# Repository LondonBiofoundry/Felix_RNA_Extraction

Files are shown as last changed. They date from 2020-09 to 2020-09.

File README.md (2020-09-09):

# Felix_RNA_Extraction
Extraction script for running RNA extraction using multiple manufacturer kits

# Hardware requirements
- CyBio FeliX Liquid Handler (Analytik Jena OL5015-24-100)
- 1x CyBio Head R96/1000 μl (Analytik Jena*)
- 2x 96-channel magazine (Analytik Jena OL3396-352-25*)
- 2x 97 mm Support (Analytik Jena OL3317-11-105*)
- 1x CyBio FeliX Gripper (Analytik Jena*)
- 1x 37 mm Support (Analytik Jena OL3317-11-120*)
- 1x Magnum FLX Enhanced magnet adapter (Alpaqua*)
- 1x BioShake D30-T elm with deep well adapter (QInstruments 2016-0518; note: *not* included in Extraction Set)
- 1x Magic Tip Thing (one or two spares are probably desirable, 3D-printed STL file included in repository)
- Laptop with a minimum of two USB ports, running Windows (Windows 10 has been confirmed to work)

&ast; included in Analytik Jena Extraction Set OL5015-25-120

# Consumable requirements per kit
- 2x 1000 μl Tecan-style filter tips (Analytik Jena OL3811-25-939-F)
- 2x protective plate (Analytik Jena 31-01641)
- 7x 96-well 2 ml deep-well plates (e.g. ThermoFisher KingFisher Flex A43075)
- 1x 96-well elution plate (e.g. FrameStar 96 well skirted PCR plate 4titude 4ti-0960)
- 1x 96 reaction extraction kit (see below for supported kits)

# Software
- Analytik Jena Composer - with support for Bioshake D30-T elm and CyBio Head R96/1000 μl, confirmed with Windows 10
- Extraction script (v16.bms)

# Supported Extraction Kits
- innuPREP Virus DNA/RNA Kit - FX (Analytik Jena 845-FX-2096096, 845-KS-4800)
- Maxwell HT Viral TNA - Custom (Promega AX2340)

# Instructions
- the file `instructions.pdf` describes the procedure for preparing with the innuPREP Virus DNA/RNA kit or the Maxwell HT Viral TNA kit.

# 3D printing
- the Magic Tip Thing permits a more reliable transfer of tips from their packaging into the magazine
- printed using an FDM printer (Prusa MK3S) with 0.2 mm layer height, no supports
- print the files `Ejector.stl` and `Retainer.stl` which will slot into each other when in use

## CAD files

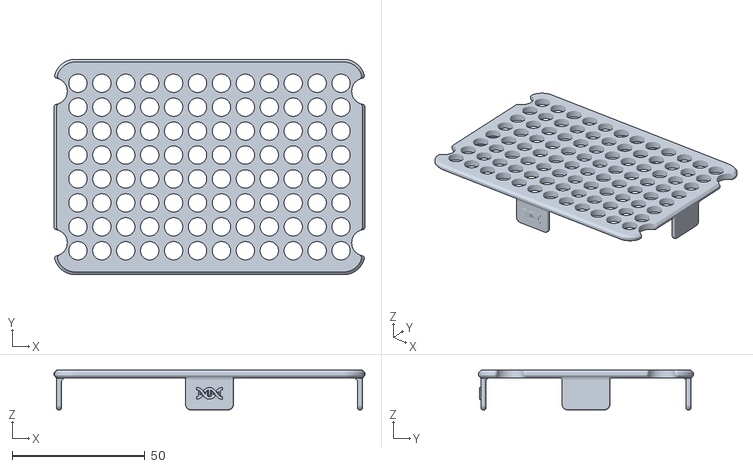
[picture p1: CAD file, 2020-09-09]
Ejector.stl
117.0 x 81.0 x 15.0

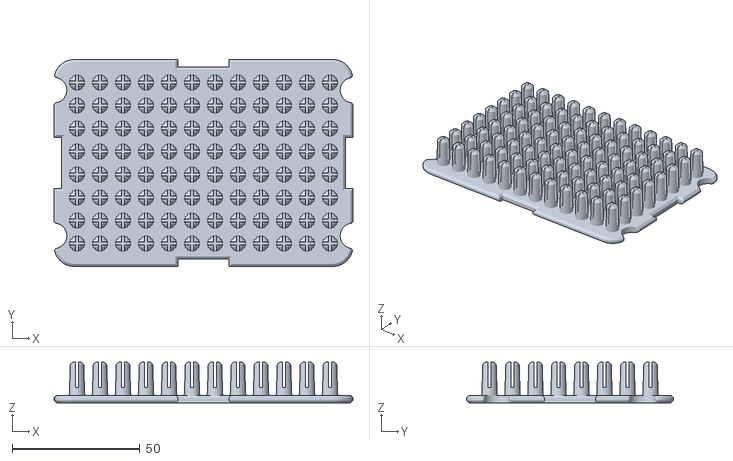
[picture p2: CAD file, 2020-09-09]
Retainer.stl
117.0 x 81.0 x 16.0

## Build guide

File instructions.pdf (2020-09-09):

Automated RNA extraction using a Felix liquid handling robot

Current version: | 16
Last updated: | April 24, 2020
Kits: | innuPREP Virus DNA/RNA Kit – FX (Analytik Jena)
| Maxwell HT Viral TNA (Promega)
The M⁴
team: | Marta Ciechonska, Michael Crone,
| Miles Priestman, Marko Storch
Contact for support: m.priestman13@imperial.ac.uk

## Contents

1 Preparing tips | 2
2 innuPREP Virus DNA/RNA Kit (Analytik Jena) | 3
3 Maxwell HT Viral TNA Kit (Promega) | 7
4 Running the protocol | 10
5 Troubleshooting | 11

1

Automated RNA extraction using a Felix liquid handling robot

## 1 Preparing tips

Prepare 2 × 1000 µl tip trays:

– Prepare the 97 mm metal support (OL3317-11-105) by placing the plastic tip protector into the base (this prevents cross-contamination). – Open the plastic tip box.
– Place the tip converter (OL3396-352-25) over the top of the tips.
– Invert the box onto a flat surface.
– Remove the white plastic insert from the tips.
– Slide the black magazine (OL3810-13-024) over the tips, with the metal rods pointing downwards.
– Invert the tips again, and remove the tip converter.
– Place the tips onto the 97 mm metal support.
– Place the supported tips into the Felix at positions 2 or 5 (centre of the lower deck).

Proceed to prepare input plates according to which kit you are using, there are minor dierences so please double-check you are following the correct section.

Automated RNA extraction using a Felix liquid handling robot

## 2 innuPREP Virus DNA/RNA Kit (Analytik Jena)

Manufacturer: AnalytikJena
Cat No: | 845-KS-4800

Please note that the protocols for a 400 µl sample volume and a 200 µl sample volume are dierent.

Note the dierent volume of Carrier Mix added to Lysis Solution V.

The 200 µl protocol also uses one less plate (Plate 3). For simplicity, the plate numbering system is preserved between all protocols to aid in placement on the Felix deck.

### 2.1 Kit preparation

Prepare the innuPREP Virus DNA/RNA Kit contents as necessary:

– Add 1.5 ml ddH2O to the vial of lyophilised proteinase K, mix thoroughly, store at −20 ◦C.
– Add 1.25 ml RNase-free water to the vial of lyophilised Carrier Mix, mix thoroughly, store at −20 ◦C; do not freeze/thaw more than 3 times.
– Add 72 ml absolute ethanol to Washing Solution B2, mix thoroughly. – Vigorously shake MAG suspension, or vortex for 30 s before use.

### 2.2 Plate preparation – 400 µl sample volume

Make sure that you are using 400 µl sample volume, otherwise, skip to Section 2.3: Plate preparation – 200 µl sample volume (pg. 4)

– Add 1.3 ml Carrier Mix to 52 ml Lysis Solution V, store at 4

◦C (maximum
7 days).

Prepare 96-well deep-well plates (provided in the kit):

Automated RNA extraction using a Felix liquid handling robot

Plate 1: Lysis/Sample

– 400 µl Lysis Solution/Carrier Mix – 400 µl liquid sample
– 50 µl proteinase K

Plate 2: Process

– 450 µl Binding Solution V – 50 µl MAG Suspension

Plate 3: Binding

– 450 µl Binding Solution V

Plate 4: Washing Solution A

– 1100 µl Washing Solution A

Plate 5: Washing Solution B2

– 1100 µl Washing Solution B2

Plate 6: Elution

– Leave empty

Plate 7: Water

– 600 µl RNase-free water

Prepare Plate 8: Final elution which can be an empty 96-well PCR plate (any 96-well labware should work, but please confirm before trying new plates).

### 2.3 Plate preparation – 200 µl sample volume

Make sure that you are using 200 µl sample volume, otherwise, skip to Section 2.2: Plate preparation – 400 µl sample volume (pg. 3)

– Add 1.75 ml Carrier Mix to 35 ml Lysis Solution V, store at 4

◦C (maximum 7 days).

Prepare 96-well deep-well plates (provided in the kit):

Automated RNA extraction using a Felix liquid handling robot

Plate 1: Lysis/Sample

– 200 µl Lysis Solution/Carrier Mix – 200 µl liquid sample
– 50 µl proteinase K

Plate 2: Process

– 450 µl Binding Solution V – 50 µl MAG Suspension

Plate 4*: Washing Solution A

(*Plate 3 is omitted)
– 1100 µl Washing Solution A

Plate 5: Washing Solution B2

– 1100 µl Washing Solution B2

Plate 6: Elution

– Leave empty

Plate 7: Water

– 600 µl RNase-free water

Prepare Plate 8: Final elution which can be an empty 96-well PCR plate (any 96-well labware should work, but please confirm before trying new plates).

### 2.4 Deck layout

Place plates onto the Felix according to the scheme below.

Automated RNA extraction using a Felix liquid handling robot

Bottom Deck

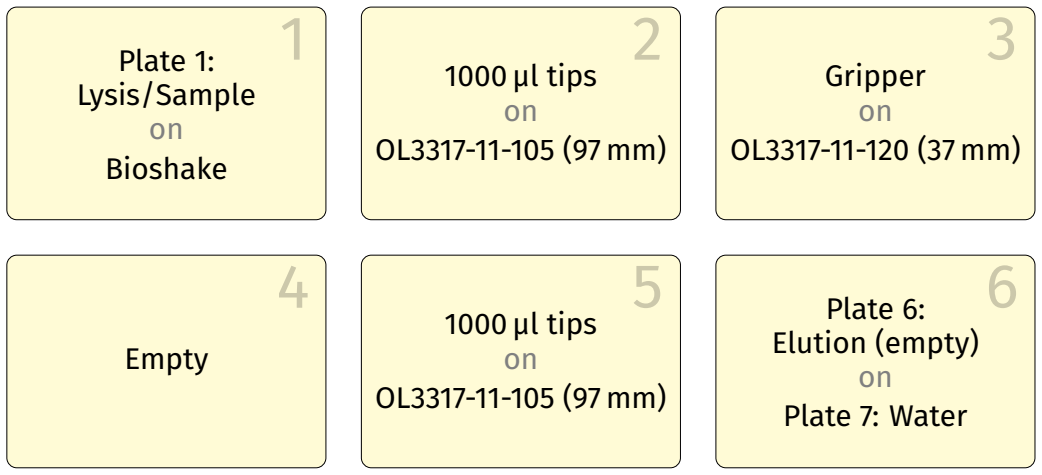
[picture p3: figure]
Plate 1:; Lysis/Sample on Bioshake; 1000 µl tips on OL3317-11-105 (97 mm); Gripper on OL3317-11-120 (37 mm); Empty; Plate 6:; Elution (empty) on Plate 7: Water

Top Deck

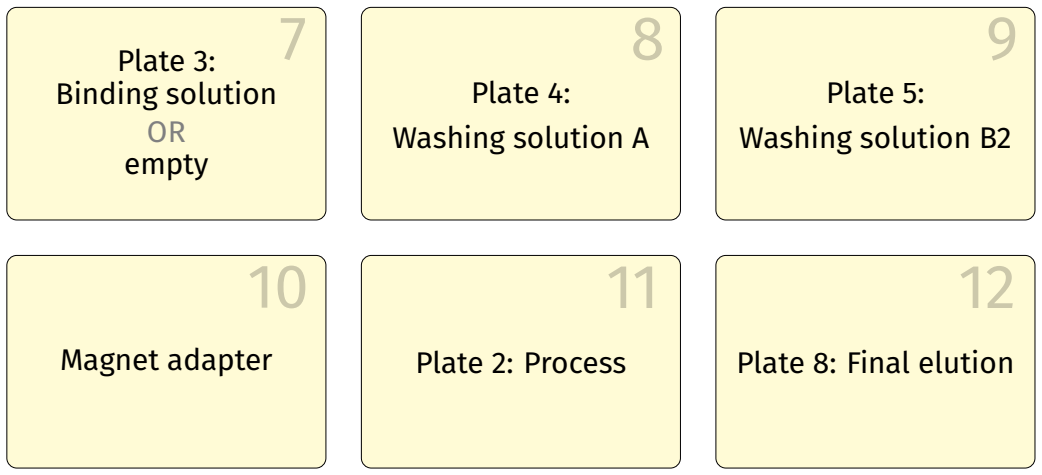
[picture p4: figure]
Plate 3:; Binding solution OR empty; Plate 4:; Washing solution A; Plate 5:; Washing solution B2; Magnet adapter; Plate 2: Process; Plate 8: Final elution

Ensure that the plates are aligned with the A1 well in the top left corner and are well constrained by the metal posts at each Felix deck position.

Ensure that the Gripper is oriented with the category number label facing towards you.

Automated RNA extraction using a Felix liquid handling robot

## 3 Maxwell HT Viral TNA Kit (Promega)

Manufacturer: Promega
Cat No: | AX2340

### 3.1 Kit preparation

Prepare the Maxwell HT Viral TNA Kit contents as necessary:

– Add 77 ml isopropanol to 4/40 Wash.
– Add 35 ml absolute ethanol to Alcohol Wash Buer.
– Add 35 ml isopropanol to Alcohol Wash Buer.
– Prepare 50 ml fresh 80 % ethanol with nuclease-free water. – Vigorously shake MagneSil Red magnetic beads before use.

### 3.2 Plate preparation

Prepare 96-well deep-well plates:

Plate 1: Lysis/Sample

– 300 µl Lysis Buer
– 200 µl liquid sample
– 30 µl proteinase K

Plate 2: Process

– 600 µl isopropanol
– 20 µl MagneSil Red

Plate 3: 4/40 Wash

– 300 µl 4/40 Wash

Plate 4: Alcohol Wash

– 300 µl Alcohol Wash

Plate 5: 80 % ethanol

– 460 µl 80 % ethanol

Plate 6: Elution

– Leave empty

Plate 7: Water

– 200 µl RNase-free water

Automated RNA extraction using a Felix liquid handling robot

Prepare Plate 8: Final elution which can be an empty 96-well PCR plate (any 96-well labware should work, but please confirm before trying new plates).

### 3.3 Deck layout

Place plates onto the Felix according to the scheme below.

Bottom Deck

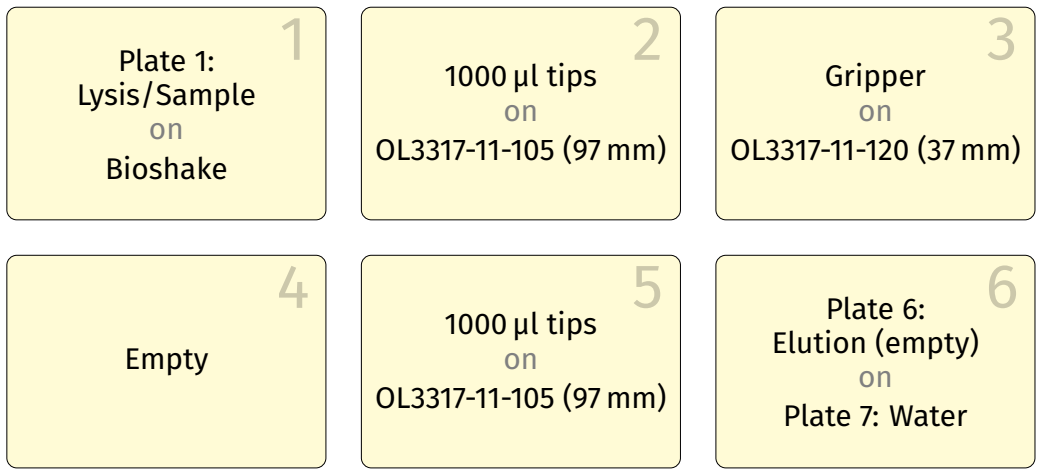
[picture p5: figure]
Plate 1:; Lysis/Sample on Bioshake; 1000 µl tips on OL3317-11-105 (97 mm); Gripper on OL3317-11-120 (37 mm); Empty; Plate 6:; Elution (empty) on Plate 7: Water

Automated RNA extraction using a Felix liquid handling robot

Top Deck

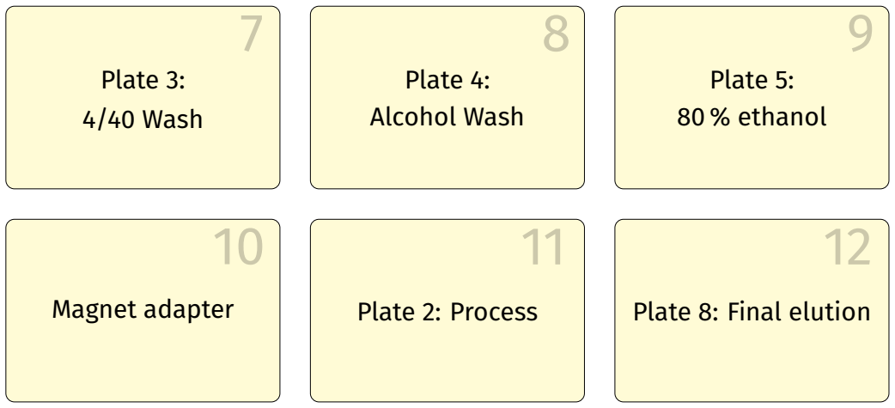
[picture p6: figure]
Plate 3:; 4/40 Wash; Plate 4:; Alcohol Wash; Plate 5:; 80 % ethanol; Magnet adapter; Plate 2: Process; Plate 8: Final elution

Ensure that the plates are aligned with the A1 well in the top left corner and are well constrained by the metal posts at each Felix deck position.

Ensure that the Gripper is oriented with the category number label facing towards you.

Automated RNA extraction using a Felix liquid handling robot

## 4 Running the protocol

– Open CyBio Composer eXtract software from the shortcut on Desktop).
– When prompted, select the profile with Bioshake.
– From the File menu, open the v16.bms.
– This file can be accessed from the shortcut on the desktop to “user files” in the Extraction_Protocols_Felix folder.
– Turn on the Felix and ensure that the door is closed.
– Ensure the Bioshake displays a green light, indicating a good connection.
– Press the green start button.
– The protocol may request calibration, press OK.
– You will be asked to select which kit you are using, select appropriately.
– If using innuPREP Virus DNA/RNA Kit – FX, you will be prompted to select the sample volume you are using.
– A short confirmation will be displayed to ensure you have selected the correct kit.
– After initialisation, the protocol will ask for confirmation that you have placed the required plates in the correct locations.
– Verify that the plates are correctly positioned, and press OK to start the protocol.
– Wait for up to 72 min (∼60 min for 200 µl sample volume).
– Remove the final elution plate from position 12 (bottom right of the top deck) for downstream processing.
– Switch o the Felix.
– Discard used labware and tips.

It is a good idea to power cycle the Felix and the Bioshake between each run (at a minimum every day) to force recalibration of the Felix.

Do not change the USB port on the laptop for the Felix connection, this can cause connectivity issues.

Frequent cleaning using RNaseZap™ or similar products is recommended.

Automated RNA extraction using a Felix liquid handling robot

## 5 Troubleshooting

In the unlikely event of system failure, the robot can be recovered from a variety of states, a number of scripts are provided to recover from such states. These scripts can be found in the troubleshooting directory.

Turning the Felix o then on, and closing and re-opening Composer can often fix problems not listed below. Please do not hesitate to contact me at m.priestman13@imperial.ac.uk if there are any other issues at all.

Bioshake ELM locked

The Edge Locking Mechanism (ELM) is the four pins on the Bioshake that lock the plate in place whilst it is shaking. In the event that the pins are locked at start-up (preventing a fresh plate from being placed), you can run the script unlock_bioshake.bms which should move the pins to their unlocked position.

Head blocks deck movement after shutdown

The head can be moved to the highest position by running move_head.bms.

Alternatively, to move the head manually, open the Felix door and hold the up button until the green light starts to flash. Release the button and press it again rapidly to start moving the head upwards. Perform the same operation with the down button to move the head downwards.

Tips still loaded

Empty the Felix, place an empty 97 mm support (OL3317-11-105) onto deck position 5, run unload_tips.bms.

Automated RNA extraction using a Felix liquid handling robot

Gripper loaded without plate

Empty the Felix, place an empty 37 mm support (OL3317-11-120) onto deck position 3, run unload_gripper.bms.

Gripper loaded with plate

Empty the Felix, place an empty 37 mm support (OL3317-11-120) onto deck position 3, run unload_plate.bms.
